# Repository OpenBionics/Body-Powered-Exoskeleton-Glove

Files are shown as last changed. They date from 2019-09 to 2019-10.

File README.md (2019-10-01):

# Body Powered Exoskleton Glove

**Title:** A Soft, Body-Powered Exoskleton Glove for Grasping Capabilities Enhancement

**Description:** 
<p align="justify"> Soft, under-actuated and compliant robotic exo-gloves have received an increased interest over the last decade. Possible applications of these systems range from augmenting the capabilities of healthy individuals to restoring the mobility of people that suffer from paralysis or stroke. Despite the significant progress in the field, most existing solutions are still heavy and expensive, they require an external power source to operate, and they are not wearable. In this project, we focus on the development of an adaptive (underactuated and compliant), tendon-driven, wearable exoskeleton glove and we propose a compact, affordable and lightweight assistive device that provides grasping capabilities enhancement to the user. This project was developed in collaboration with the New Dexterity research team (University of Auckland, New Zealand). </p>  

<p align="justify"> The body-powered exo-glove was designed to enhance the grasping capabilities of the user, providing easiness and intuitiveness of operation, with long autonomy, low maintenance, and low cost. The device consists of four different parts: the differential module, the soft glove, the tendon tensioning and adjustment mechanism, and the harness (see Figure below). </p>  

<p align="justify"> The differential module is a solution for tendon tensioning and even distribution of the grasping forces for the participating fingers. The particular differential mechanism can also be applied to different underactuated prosthetic and orthotic systems. Differentials based on the whiffletree mechanism are widely used in underactuated robot hands. The differential is divided into three different parts: the ratchet clutch, the linear ratchet, and the spring loaded whiffletree mechanism. The ratchet clutch mechanism consists of a ratchet-pulley block for tendon wrapping, a pawl that blocks the rotation of the ratchet in one direction and an elastic element that acts as a spring and pushes the pawl against the ratchet teeth, constraining its motion in the other direction. This mechanism allows a fine and precise adjustment of the tendon length (with a precision of 0.87 mm). The purpose of using this mechanism is to adjust the length of multiple tendons that are routed through the tendon routing tubes and reach the glove. In order to keep the tendon tensioned for a long time, a linear ratchet was used. This mechanism guarantees that the tendon is locked in one position until the mechanism is used again. This mechanism consists of several "V" shape teeth arranged on a row, a lever, a rail, a base, and two springs. The rail is fixed to the differential module through screws and the base can slide on the rail guaranteeing that the motion of the base always happens on a single axis. When the upper cable is pulled, the lever is pushed by a spring against the teeth until the system reaches the desired position. Then, the lever slides into one of the "V" shape teeth locking the mechanism and keeping the tension constant. When the system is re-engaged, the lever is pulled again to the channel and a spring that connects the base to the differential module walls pulls the base until the lever reaches its lowest position and the tendon returns to its initial tension. When the upper cable is pulled again the cycle is reinitialized.  The ability to keep the tendons tensioned for long periods of time is of paramount importance for underactuated and body-powered systems, since in other tendon-driven, motorized solutions (e.g., fully-actuated systems) the dedicated motors can adjust the tensioning of the tendons and hold the load while the grasping and manipulation of the objects take place. </p>  

<p align="justify"> The body-powered mechanism allows the transmission of forces from the upper body (e.g., the shoulders) to the index, middle, and thumb fingers through the tendon routing system. Simple body movements can increase the tension of the tendon, actuating the soft exo-glove. The differential mechanism is used to evenly distribute the forces to the fingers. In order to operate the device, this cable must be accurately tensioned and for this purpose, a tension adjustment mechanism was designed. The mechanism consists of a base where the parts are connected, a lever, a pulley with rectangular teeth, a cover and a retractable reel. After wearing the mechanism, the user presses a lever and the cable on the reel (separate from the tendon) rotates the pulley in the counterclockwise direction wrapping the actuation tendon around it and tensioning it. The plastic cover guarantees that the cable does not slip out of the pulley channel. </p>  

<p align="justify"> The proposed harness was chosen for the body-powered device because it is comfortable and helps to keep the shoulders aligned. When the right arm or the shoulders move transmitting forces to the main cable, the differential is pulled and the artificial tendons of the fingers are tensioned. These tendons are in charge of moving the fingers and they are made out of a low friction braided fiber of high-performance UHMWPE (Ultra-High Molecular Weight Polyethylene). One end of the tendon is terminated on the differential mechanism and the other end on a stainless steel structure at each fingertip. It must be noted that the execution of tasks with the body-powered mechanism takes longer due to the longer body compensation motions that are required to actuate the exo-glove. The body-powered exo-glove was designed to be as simple and straightforward as possible to allow people to use it without intense training. The device can be adjusted to all body types and sizes. The personalization occurs only for the glove and the harness because the size of these items depends on the user's height and weight. </p>  

<p align="justify"> The prototype of the body powered mechanism costs less than 100 USD to produce and weighs less than 400 g. To the best of our knowledge this is the lightest among all the assistive exo-gloves currently found in the literature. It is important to highlight that this solution can be extended to different actuation units. The force transmission from the shoulder to the fingertips could be executed by other members or external systems if the person cannot use other body parts (e.g., a motor could replace the tension adjustment mechanism to tension the cable that comes from the spring loaded differential mechanism). For further information about our projects visit https://openbionics.org/ </p>  

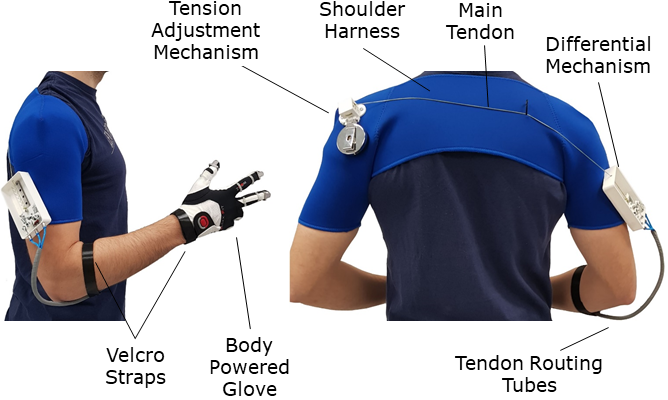
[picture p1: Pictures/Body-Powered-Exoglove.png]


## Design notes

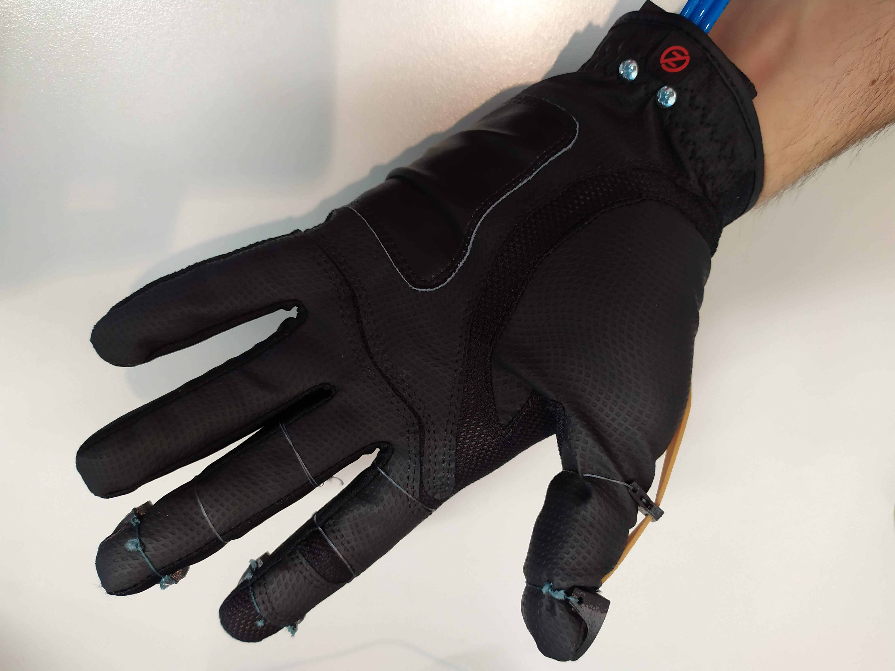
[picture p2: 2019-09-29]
Pictures/Glove_1.jpg

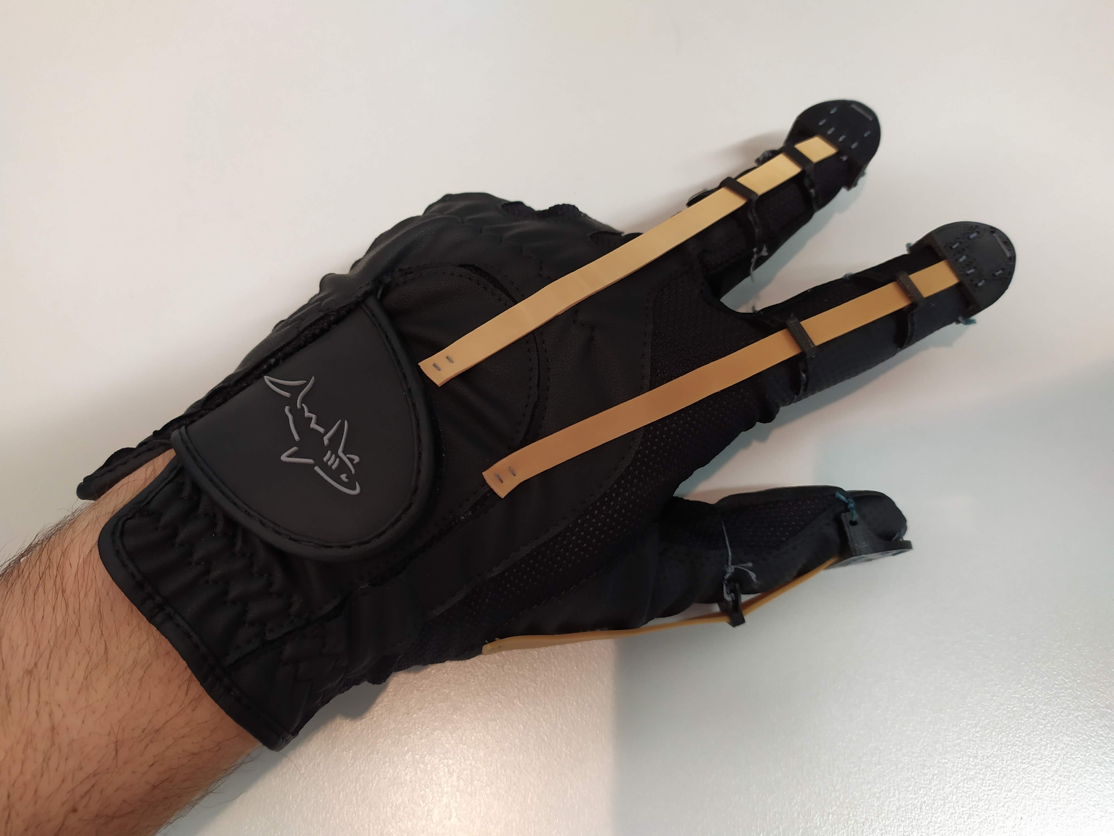
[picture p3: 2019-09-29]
Pictures/Glove_2.jpg

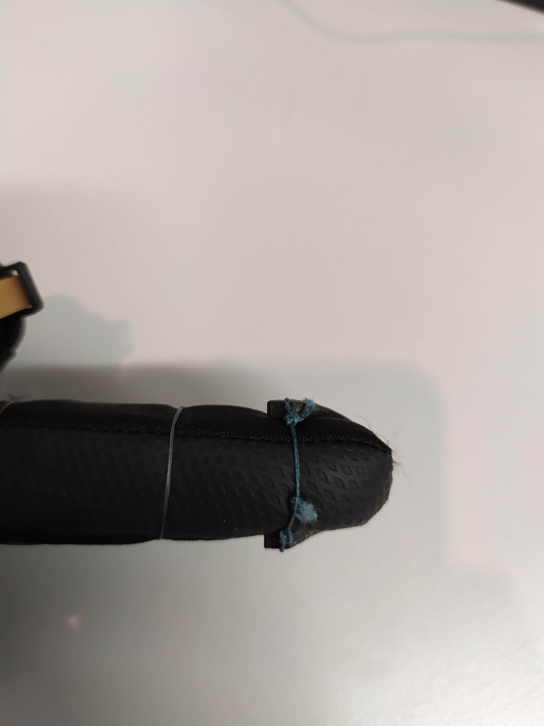
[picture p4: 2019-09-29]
Pictures/Glove_5.jpg

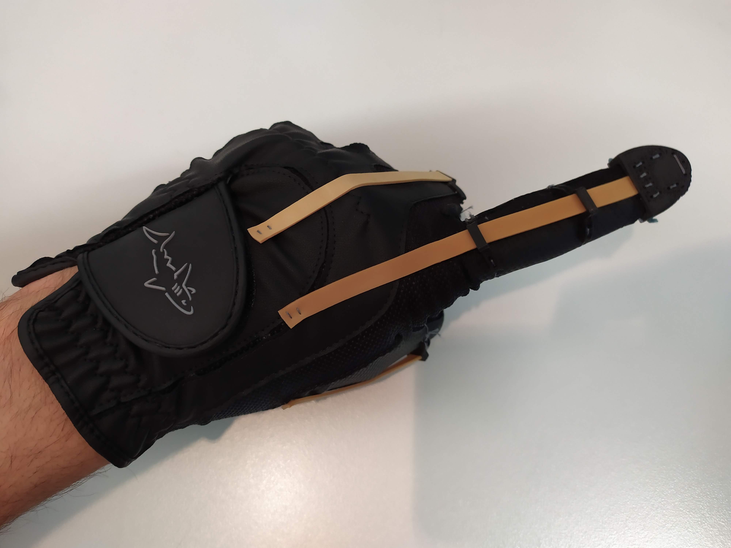
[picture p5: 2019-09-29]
Pictures/Glove_3.jpg

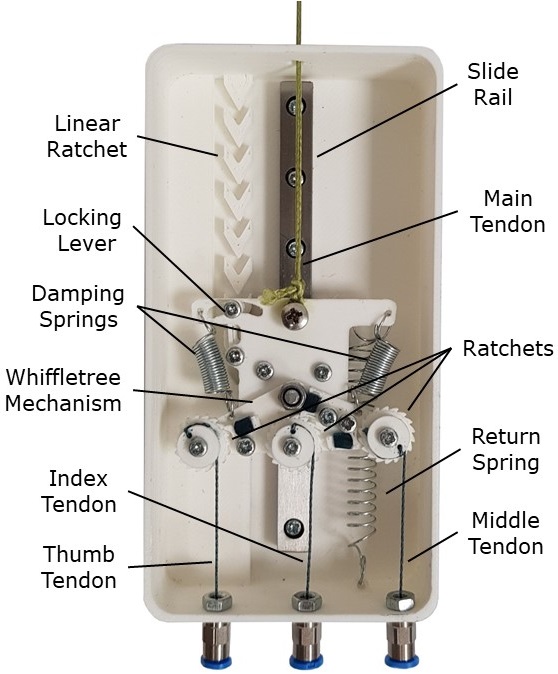
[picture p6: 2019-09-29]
Pictures/Differential_description.jpg

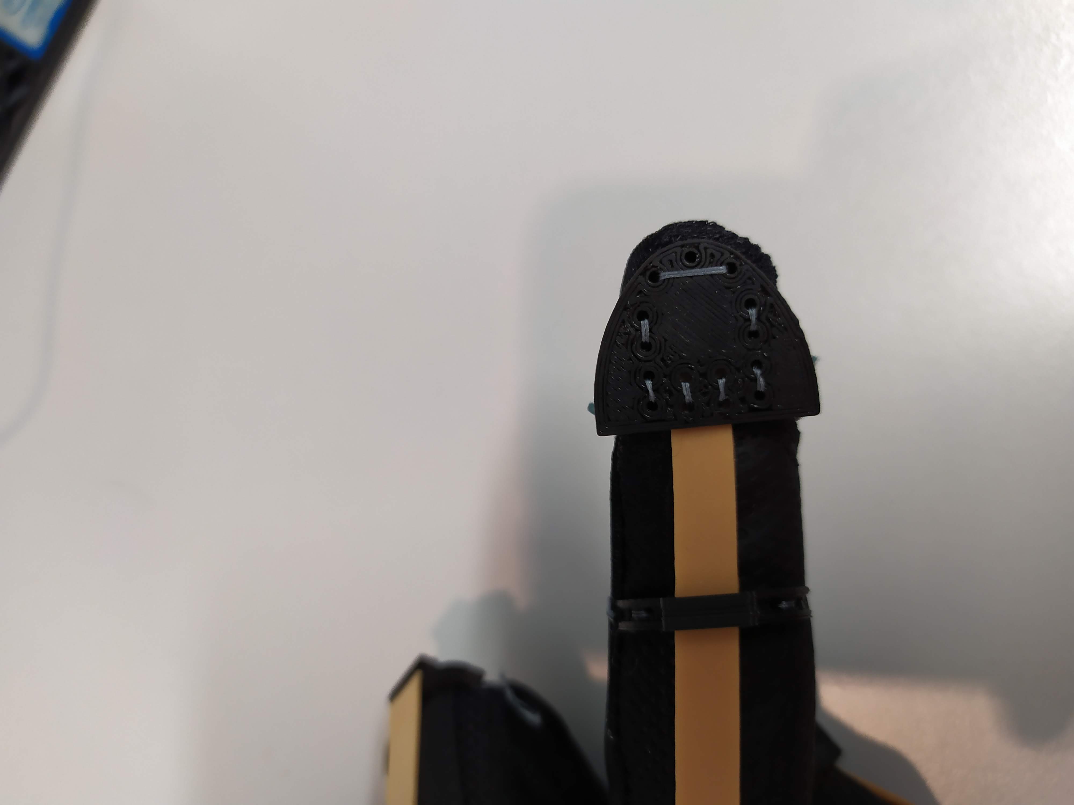
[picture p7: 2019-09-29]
Pictures/Glove_4.jpg

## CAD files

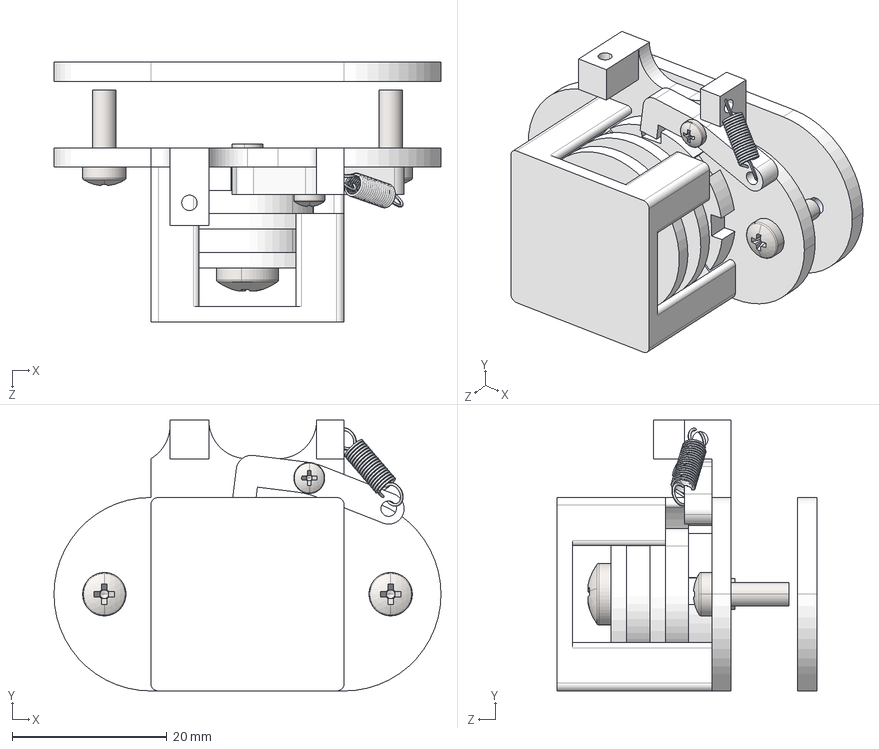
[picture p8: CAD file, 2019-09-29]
Tensioner/Glove_tensioner_Assy.STEP
50.0 x 35.0 x 33.6 mm
Lever
Pulley
Base
cover
Bottom
pan head cross recess screw_iso_ISO 7045 - M2 x 6 - Z - 6N
pan head cross recess screw_iso_ISO 7045 - M3 x 10 - Z - 10N x 2
pan head cross recess screw_iso_ISO 7045 - M4 x 16 - Z - 16N
9654K9412_STEEL EXTENSION SPRING_9654K941
7804K103_STAINLESS STEEL BALL BEARING_7804K103 x 2

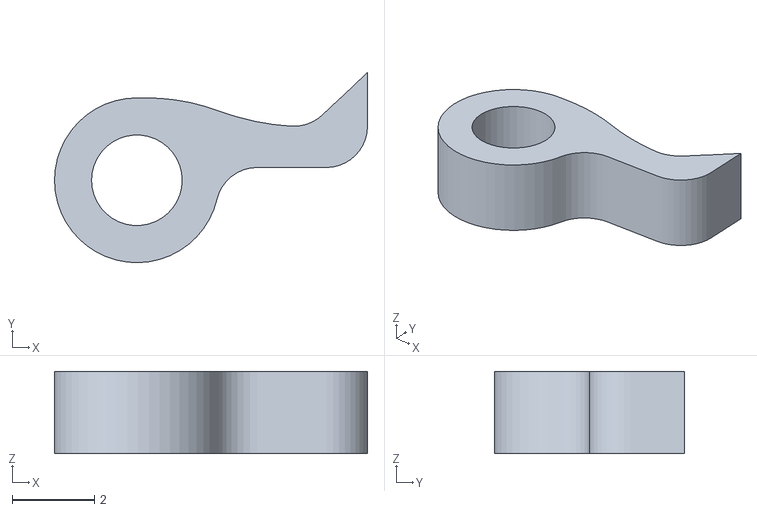
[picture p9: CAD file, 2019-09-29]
Differential/Ratchet.STL
7.60 x 4.62 x 2.00

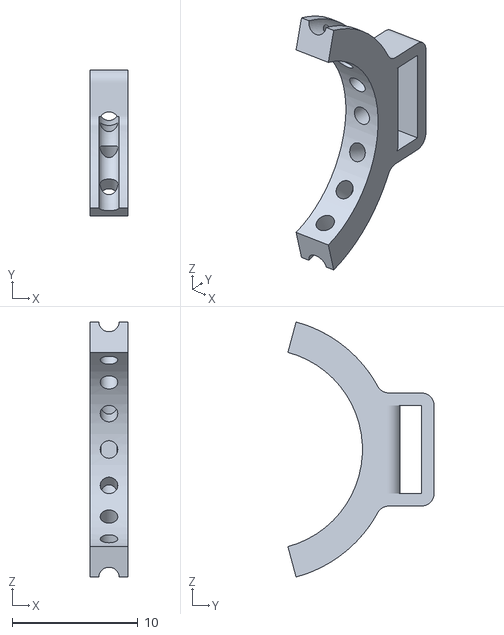
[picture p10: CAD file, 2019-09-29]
Glove/Anchor_top.STL
3.00 x 11.6 x 20.3

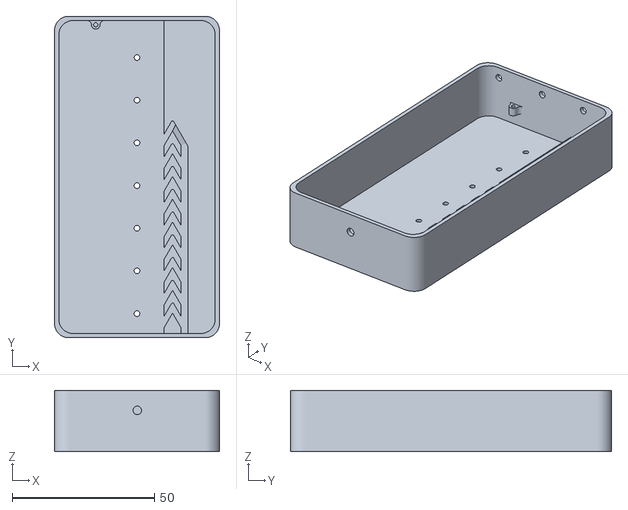
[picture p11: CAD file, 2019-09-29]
Differential/Box.STL
58.0 x 113.0 x 21.5

Glove/Nail_glove.STL
22.0 x 18.5 x 10.0

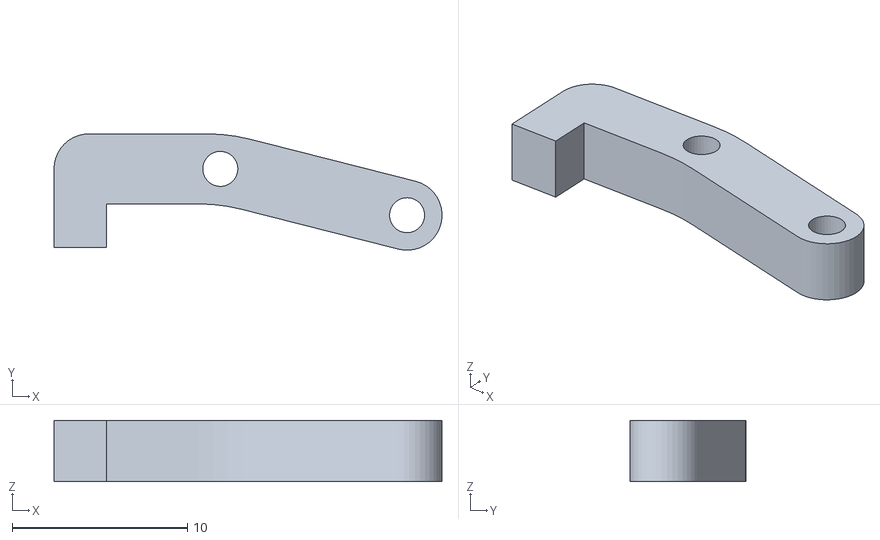
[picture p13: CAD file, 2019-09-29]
Tensioner/Lever.STL
22.2 x 6.64 x 3.50

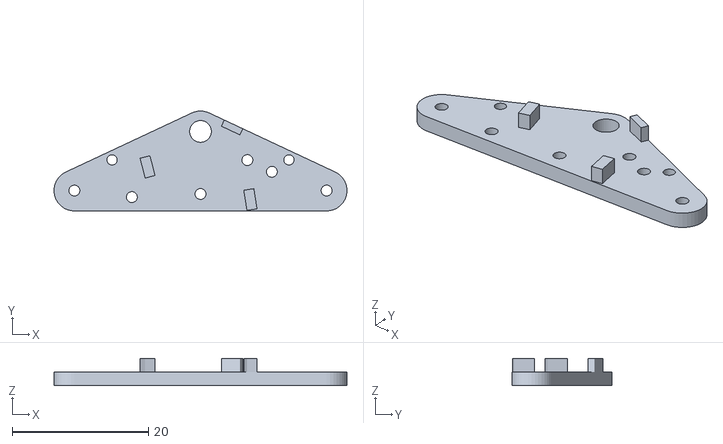
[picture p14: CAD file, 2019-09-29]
Differential/Triangle.STL
43.1 x 14.7 x 4.00

Glove/Glove_holder.STL
19.0 x 3.50 x 5.00

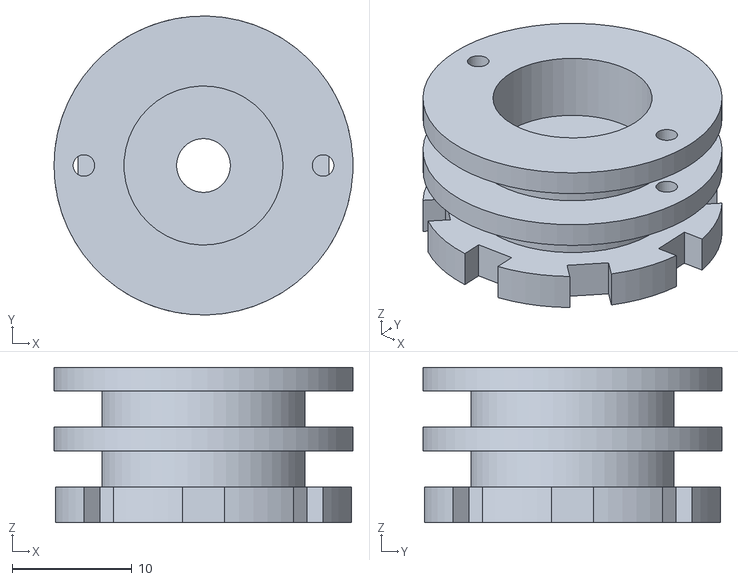
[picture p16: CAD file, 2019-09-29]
Tensioner/Pulley.STL
25.0 x 25.0 x 13.0

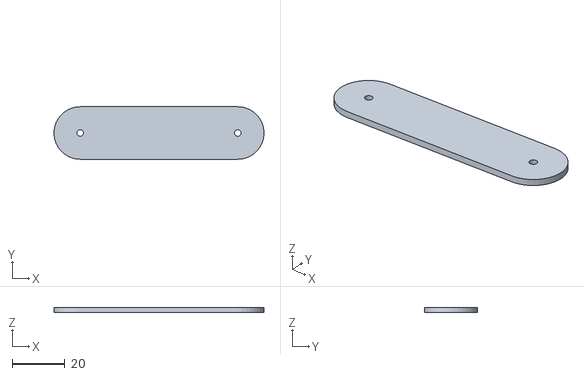
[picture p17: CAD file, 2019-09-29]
Differential/Back attachment.STL
79.9 x 20.0 x 2.00

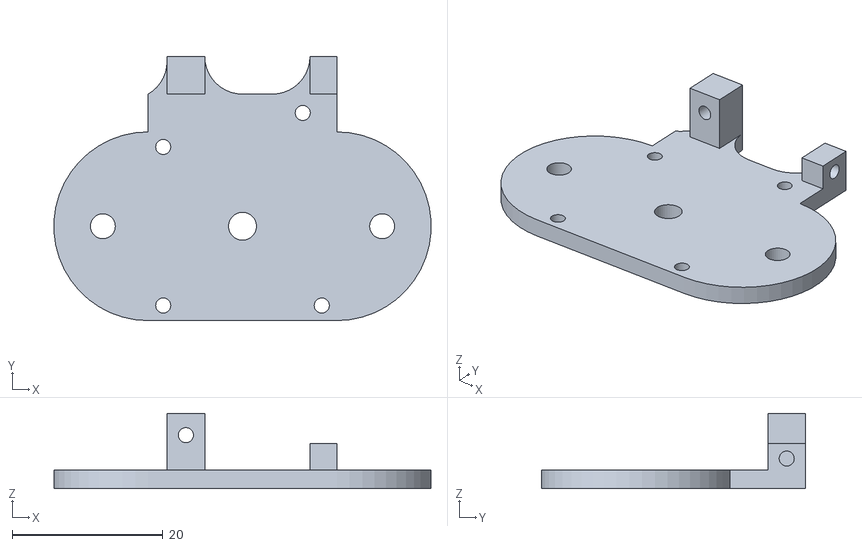
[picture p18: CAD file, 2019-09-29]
Tensioner/Base.STL
49.9 x 35.0 x 10.0

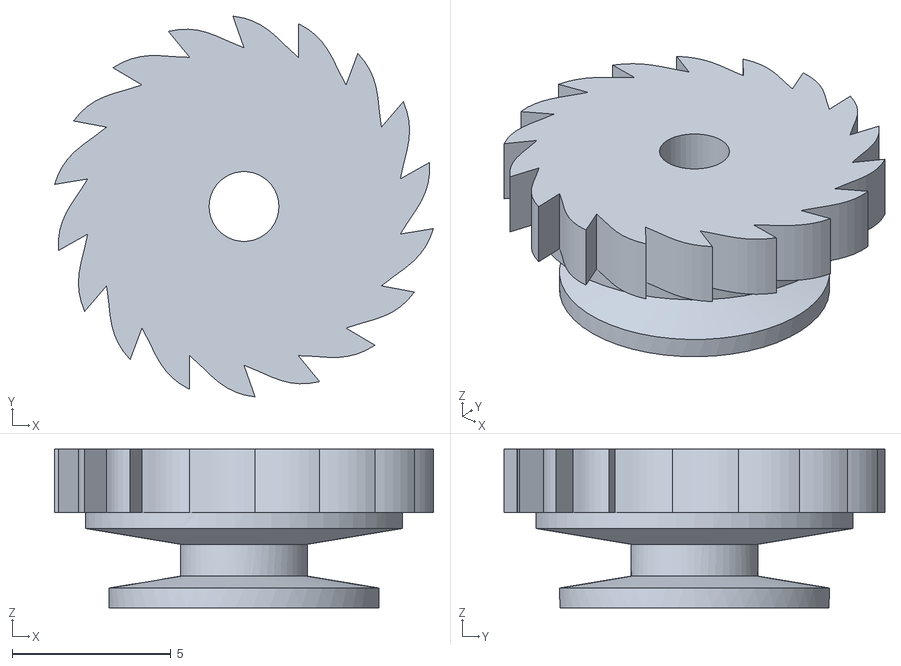
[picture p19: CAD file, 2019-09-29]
Differential/Pulley.STL
11.9 x 12.0 x 5.00

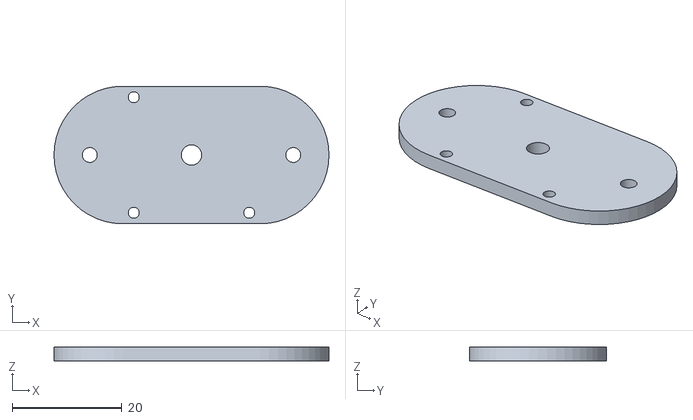
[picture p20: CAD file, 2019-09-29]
Tensioner/Bottom.STL
50.0 x 25.0 x 2.50

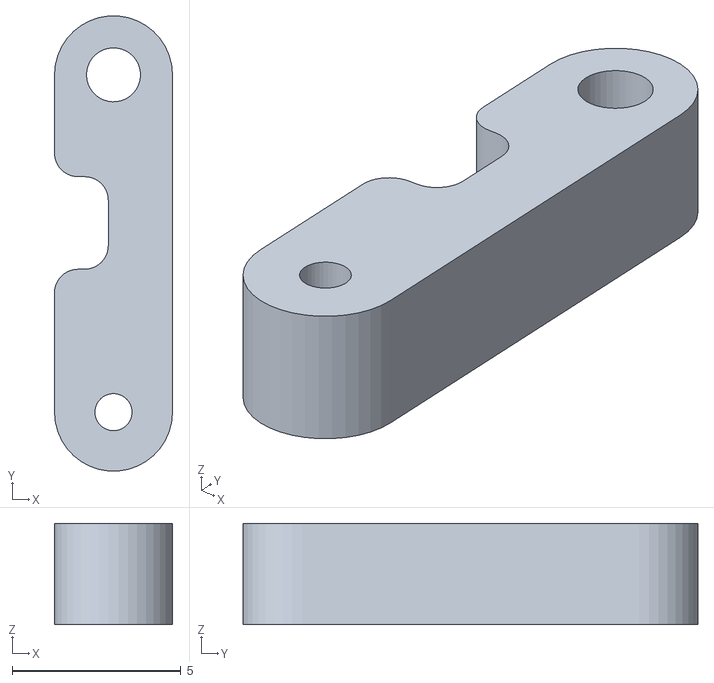
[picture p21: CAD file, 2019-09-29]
Differential/Lever.STL
3.50 x 13.5 x 3.00

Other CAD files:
Tensioner/Cover.STL
Differential/Rail attachment.STL

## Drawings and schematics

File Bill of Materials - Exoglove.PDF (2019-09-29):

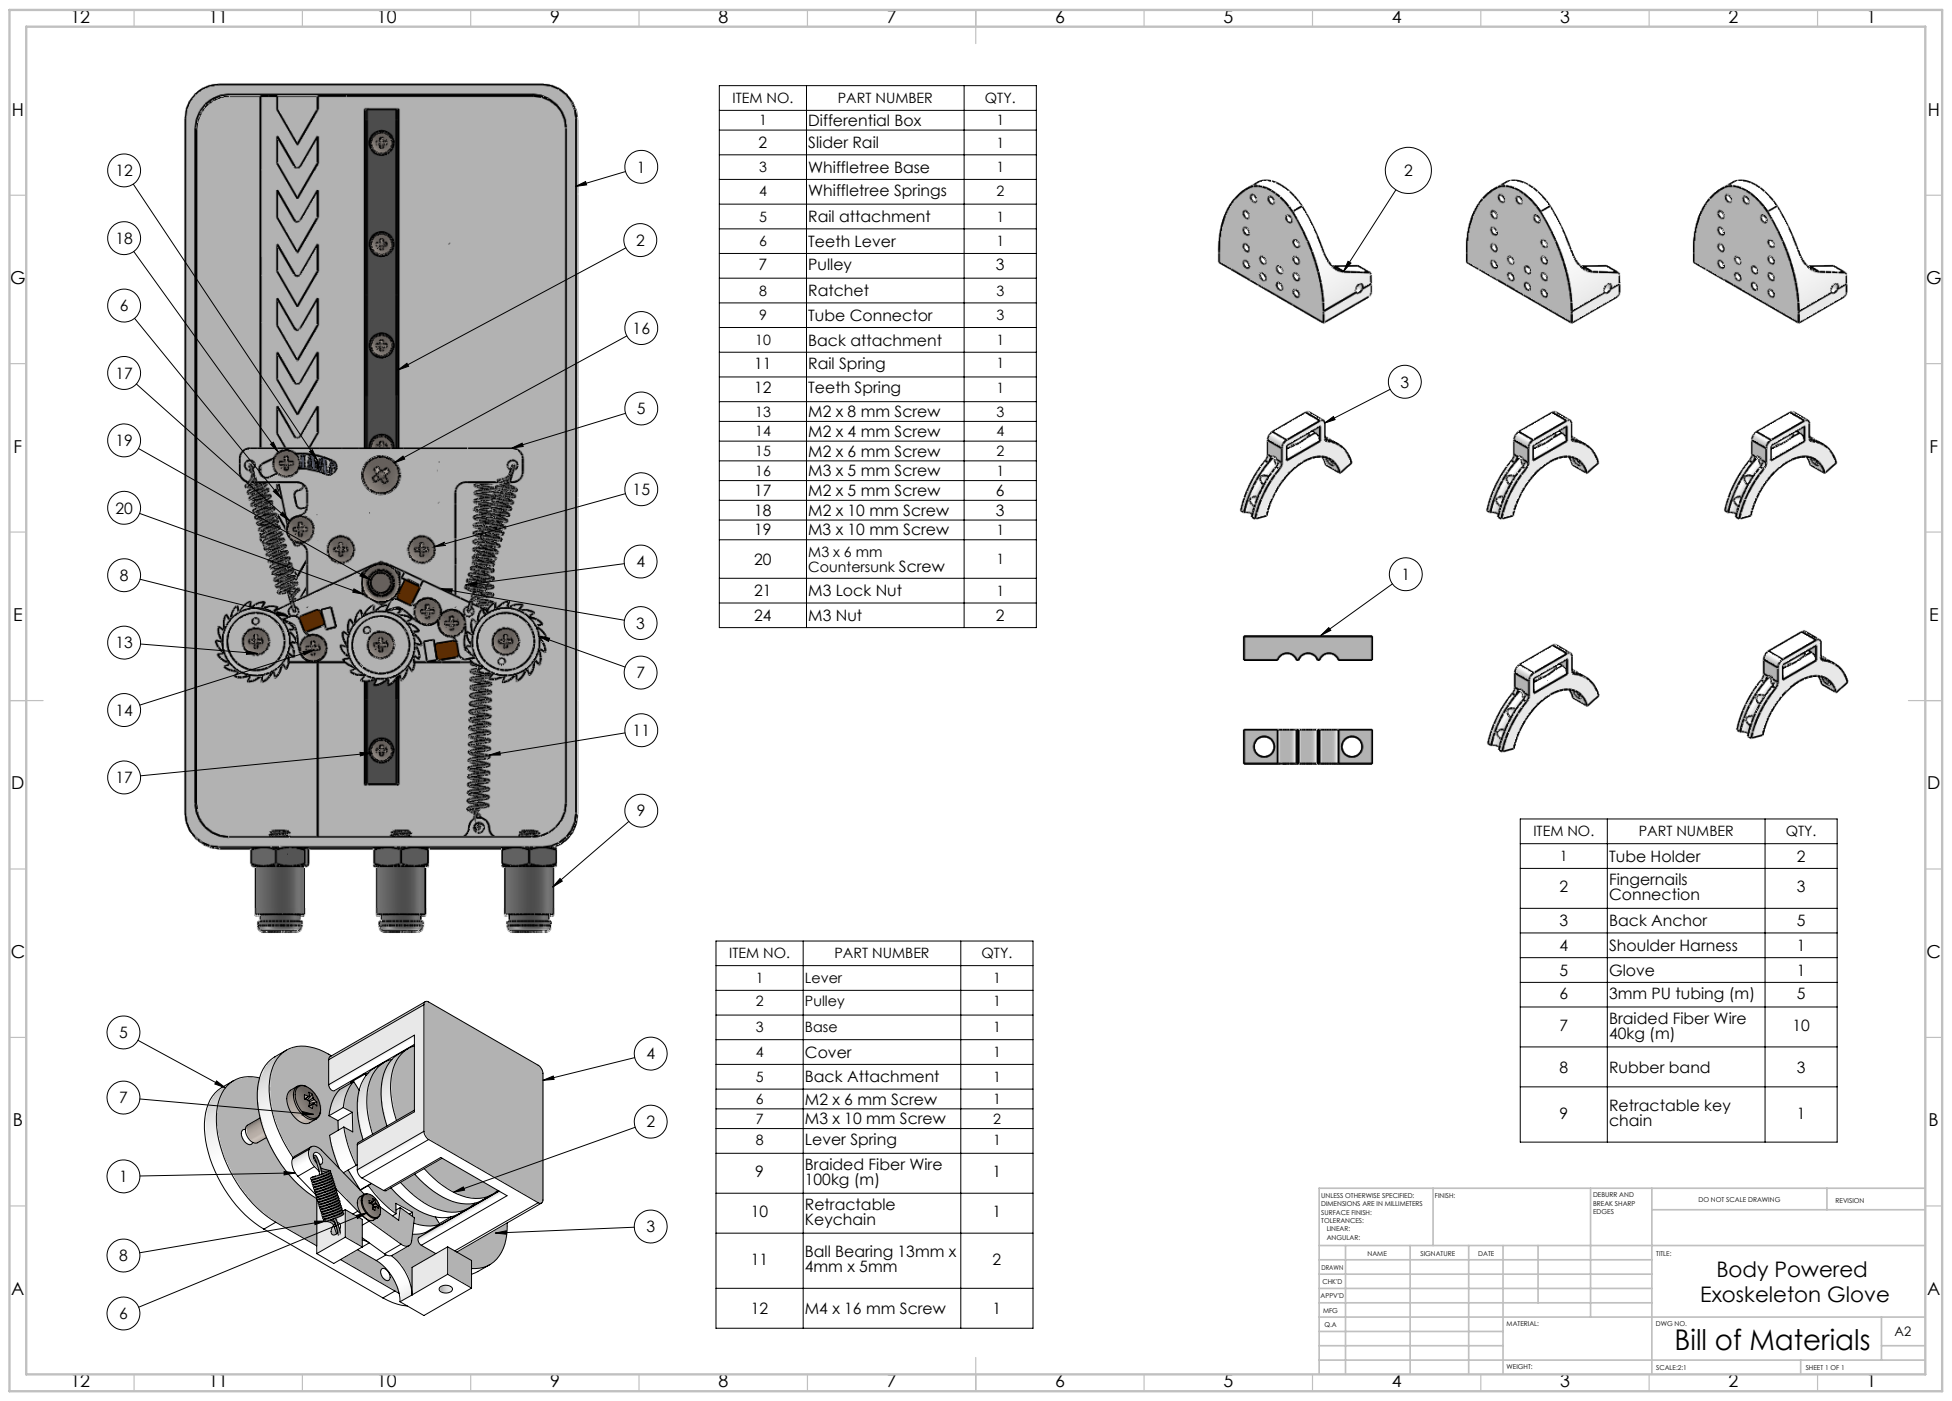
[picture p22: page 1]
ITEM NO.; PART NUMBER; QTY. 1; Differential Box; Slider Rail; Whiffletree Base; Whiffletree Springs; Rail attachment; Teeth Lever; Pulley; Ratchet; Tube Connector; Lever; Base; Cover; Back Attachment; M2 x 6 mm Screw; M3 x 10 mm Screw; Lever Spring; Braided Fiber Wire; M4 x 16 mm Screw; FINISH:; DEBURR AND; BREAK SHARP; DO NOT SCALE DRAWING; REVISION; SCALE:2:1; SHEET 1 OF 1

10 | Back attachment | 1
11 | Rail Spring | 1
12 | Teeth Spring | 1
13 | M2 x 8 mm Screw | 3
14 | M2 x 4 mm Screw | 4
15 | M2 x 6 mm Screw | 2
16 | M3 x 5 mm Screw | 1
17 | M2 x 5 mm Screw | 6
18 | M2 x 10 mm Screw | 3
19 | M3 x 10 mm Screw | 1
20 | M3 x 6 mm Countersunk Screw | 1
21 | M3 Lock Nut | 1
24 | M3 Nut | 2

ITEM NO. | Tube Holder Fingernails PART NUMBER | QTY. 1 2 2

3 | Back Anchor | 5
4 | Shoulder Harness | 1
5 | Glove | 1
6 | 3mm PU tubing (m) | 5
7 | Braided Fiber Wire 40kg (m) | 10

8 | Rubber band | 3
9 | Retractable key chain | 1

100kg (m) | 1
10 | Retractable Keychain | 1

UNLESS OTHERWISE SPECIFIED:
DIMENSIONS ARE IN MILLIMETERS
SURFACE FINISH:
TOLERANCES:
LINEAR:
ANGULAR:

11 | Ball Bearing 13mm x 4mm x 5mm | 2

NAME | SIGNATURE | DATE | TITLE: Body Powered Exoskeleton Glove

DRAWN
CHK'D

MFG
Q.A | MATERIAL: | DWG NO. Bill of Materials | A2
